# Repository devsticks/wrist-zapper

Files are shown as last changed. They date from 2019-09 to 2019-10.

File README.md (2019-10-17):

# Wrist Zapper
A portable wrist pose controlled electrocutaneous stimulator. Part of an undergraduate thesis.

Operates on an ESP32, and communicates with a companion app built on Blynk via BLE.

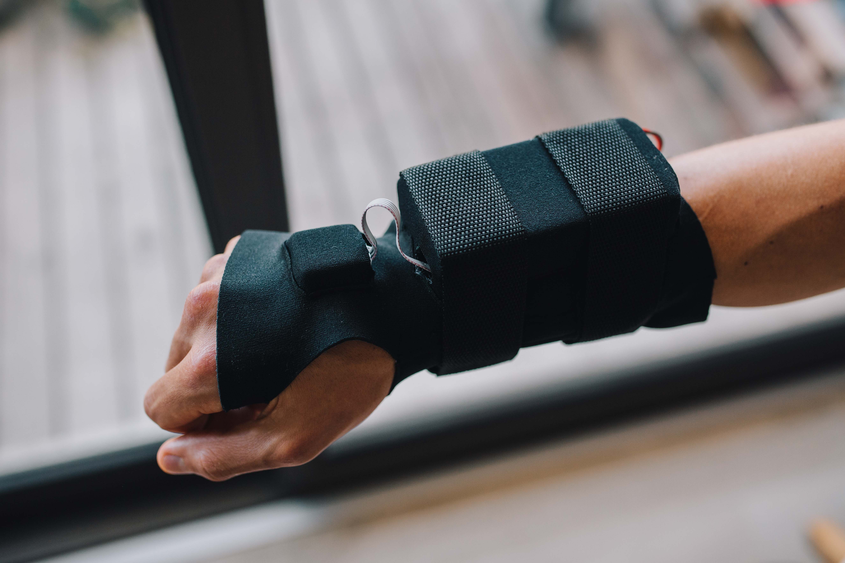
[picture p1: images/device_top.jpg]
The Wrist Zapper


If you'd like to make your own, see the build instructions [here](https://github.com/devsticks/wrist-zapper/tree/master/production_hardware/README.md).

## System Diagram

The following is a basic system diagram showing the various elements of the design and how they relate to one another:
<p align="center">
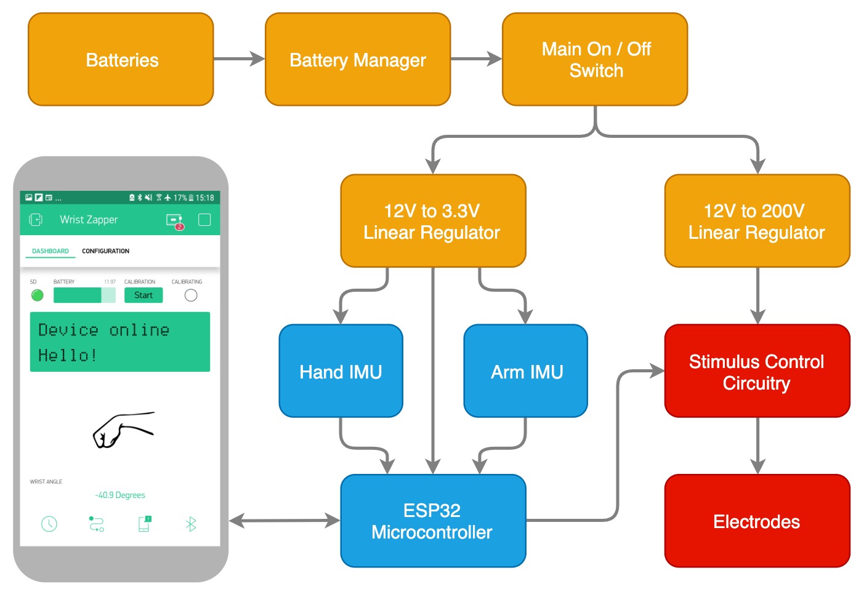
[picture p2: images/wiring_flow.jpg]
System diagram

</p>

## Bill of Materials

| Item                                                  | Part Number | Supplier  | Cost    | Quantity | Total Cost |
|-------------------------------------------------------|-------------|-----------|---------|----------|------------|
| Microcontroller (Adafruit ESP32 Feather)              | 3405        | Adafruit  | R299.25 | 1        | R299.25    |
| IMU (6 DOF)                                           | SEN-00138   | Netram    | R126.05 | 2        | R252.10    |
| Boost Convertor (12-200V, 60mA)                       | NCH6100HV   | Amazon    | R284.85 | 1        | R284.85    |
| Buck Convertor (12-3.3V, 2A)                          | MP1584      | Communica | R45.00  | 1        | R45.00     |
| NPN Transistor                                        | MJE340      | Farnell   | R10.66  | 1        | R10.66     |
| P-Channel MOSFET (400V, 3.5A)                         | FQP4P40     | Farnell   | R22.72  | 3        | R68.15     |
| SD Card Reader (Wemos D1 Mini RTC/Data Logger Shield) |             | Communica | R82.61  | 1        | R82.61     |
| Battery Manager (Comidox 3S, 12.6V, 10A)              |             | Amazon    | R38.95  | 1        | R38.95     |
| Resistor (Through-hole, 25mW, 1k)                     |             | UCT       | R0.00   | 4        | R0.00      |
| Resistor (Through-hole, 25mW, 2k2)                    |             | UCT       | R0.00   | 2        | R0.00      |
| Resistor (Through-hole, 25mW, 3k3)                    |             | UCT       | R0.00   | 1        | R0.00      |
| Resistor (Through-hole, 25mW, 10k)                    |             | UCT       | R0.00   | 1        | R0.00      |
| LED (Red, 5mm, 20mA)                                  |             | UCT       | R0.00   | 1        | R0.00      |
| LED (Green, 5mm, 20mA)                                |             | UCT       | R0.00   | 1        | R0.00      |
| Fuse (glass, 30mA)                                    |             | UCT       | R0.00   | 1        | R0.00      |
| Fuse holder                                           |             | UCT       | R0.00   | 1        | R0.00      |
| 3.7V Li-Ion Battery                                   |             | UCT       | R0.00   | 3        | R0.00      |
| Small On/Off Switch                                   | COM-00652   | Netram    | R15.00  | 1        | R15.00     |
| JST Connector (1A, 2 pin, female, 14cm)               |             | Communica | R3.04   | 4        | R12.17     |
| JST Connector (1A, 2 pin, male, 14cm)                 |             | Communica | R3.04   | 4        | R12.17     |
| Heat Shrink (Various colours, 1/8")                   |             | Communica | R0.44   | 3        | R1.32      |
| Header Connector (5 pin, female, 2.54mm, L, locking)  | XY136-05RT  | Communica | R0.91   | 2        | R1.82      |
| Header Connector (5 pin, male 2.54mm, locking)        | XY136-05HT  | Communica | R1.45   | 2        | R2.90      |
| Header Connector (2 pin, female, 2.54mm, L, locking)  | XY136-02RT  | Communica | R0.31   | 2        | R0.62      |
| Header Connector (2 pin, male 2.54mm, locking)        | XY136-02HT  | Communica | R0.55   | 2        | R1.10      |
| Ribbon Cable (10-way, 1m)                             |             | Communica | R7.36   | 0.1      | R0.74      |
| Any small jumper cable (comms core will do, 1m)       |             | UCT       | R0.00   | 1        | R0.00      |
| Strip Board (2.54mm pitch, 100x300mm)                 |             | UCT       | R70.00  | 1        | R70.00     |
| 3D Printing                                           |             |           | R120.00 | 1        | R120.00    |
|                                                       |             |           |         |          |            |
| **Total**                                             |             |           |         |          | **R1,319.40**  |

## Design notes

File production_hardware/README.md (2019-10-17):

# Build Instructions

You can make your very own Wrist Zapper - just be careful, you can really hurt yourself with one of these. 

If you want to get the cool stuff working first, follow this guide step-by-step. Otherwise go for it in any order - the steps aren't very dependent on one another. If you make your own Wrist Zapper please give me a shout - I'd love to see it!

# Table of Contents
1. [Device Electronics](#1-device-electronics)
2. [Microcontroller Code](#2-microcontroller-code)
3. [Smartphone App](#3-smartphone-app)
4. [Sleeve](#4-sleeve)
5. [Electrode](#5-electrode)
6. [Charger Electronics](#6-charger-electronics)
7. [Enclosures](#7-enclosures)
8. [Putting It Together](#8-putting-it-together)

## 1. Device Electronics

### Parts required

| Item                                                  | Part Number | Supplier  | Cost    | Quantity | Total Cost |
|-------------------------------------------------------|-------------|-----------|---------|----------|------------|
| Microcontroller (Adafruit ESP32 Feather)              | 3405        | Adafruit  | R299.25 | 1        | R299.25    |
| IMU (6 DOF)                                           | MPU6050     | Netram    | R126.05 | 2        | R252.10    |
| Boost Convertor (12-200V, 60mA)                       | NCH6100HV   | Amazon    | R284.85 | 1        | R284.85    |
| Buck Convertor (12-3.3V, 2A)                          | MP1584      | Communica | R45.00  | 1        | R45.00     |
| NPN Transistor (300V, 500mA, 20W)                     | MJE340      | Farnell   | R10.66  | 1        | R10.66     |
| P-Channel MOSFET (400V, 3.5A)                         | FQP4P40     | Farnell   | R22.72  | 3        | R68.15     |
| SD Card Reader (Wemos D1 Mini RTC/Data Logger Shield) |             | Communica | R82.61  | 1        | R82.61     |
| Battery Manager (Comidox 3S, 12.6V, 10A)              |             | Amazon    | R38.95  | 1        | R38.95     |
| Resistor (Through-hole, 25mW, 1k)                     |             | UCT       | R0.00   | 4        | R0.00      |
| Resistor (Through-hole, 25mW, 2k2)                    |             | UCT       | R0.00   | 2        | R0.00      |
| Resistor (Through-hole, 25mW, 3k3)                    |             | UCT       | R0.00   | 1        | R0.00      |
| Resistor (Through-hole, 25mW, 10k)                    |             | UCT       | R0.00   | 1        | R0.00      |
| LED (Red, 5mm, 20mA)                                  |             | UCT       | R0.00   | 1        | R0.00      |
| LED (Green, 5mm, 20mA)                                |             | UCT       | R0.00   | 1        | R0.00      |
| Fuse (glass, 30mA)                                    |             | UCT       | R0.00   | 1        | R0.00      |
| Fuse holder                                           |             | UCT       | R0.00   | 1        | R0.00      |
| 3.7V Li-Ion Battery                                   |             | UCT       | R0.00   | 3        | R0.00      |
| On/Off Switch                                         | COM-00652   | Netram    | R15.00  | 1        | R15.00     |
| JST Connector (1A, 2 pin, female, 14cm)               |             | Communica | R3.04   | 4        | R12.17     |
| JST Connector (1A, 2 pin, male, 14cm)                 |             | Communica | R3.04   | 4        | R12.17     |
| Heat Shrink (Various colours, 1/8")                   |             | Communica | R0.44   | 3        | R1.32      |
| Header Connector (5 pin, female, 2.54mm, L, locking)  | XY136-05RT  | Communica | R0.91   | 2        | R1.82      |
| Header Connector (5 pin, male 2.54mm, locking)        | XY136-05HT  | Communica | R1.45   | 2        | R2.90      |
| Header Connector (2 pin, female, 2.54mm, L, locking)  | XY136-02RT  | Communica | R0.31   | 2        | R0.62      |
| Header Connector (2 pin, male 2.54mm, locking)        | XY136-02HT  | Communica | R0.55   | 2        | R1.10      |
| Ribbon Cable (10-way, 1m)                             |             | Communica | R7.36   | 0.1      | R0.74      |
| Any small jumper cable (comms core will do, 1m)       |             | UCT       | R0.00   | 1        | R0.00      |
| Strip Board (2.54mm pitch, 100x300mm)                 |             | UCT       | R70.00  | 1        | R70.00     |
| | | | | | |
| **Total** |  |  |  |  | **R1,199.40** |

### Preparing the stripboard

Before soldering, you will need to remove portions of the stripboard in order to build the final circuit. The easiest way to mark out your stripboard is to download a copy of [this image](https://github.com/devsticks/wrist-zapper/raw/master/production_hardware/electronics/circuit_main_inverted_flipped.jpeg) and crop it so that the grid spacing on your screen matches that of your stripboard. The image at the link perfectly matches 2.54mm stripboard on a 9.7"-sized iPad screen. 

Once you have the image sized up, place your stripboard over the screen (metal side up) and mark any spots with purple crosses for removal with a marker pen, as below (this is easier to see in real life than in the image...). The task is best done in a dark room with screen brightness maximised.

<p align="center">
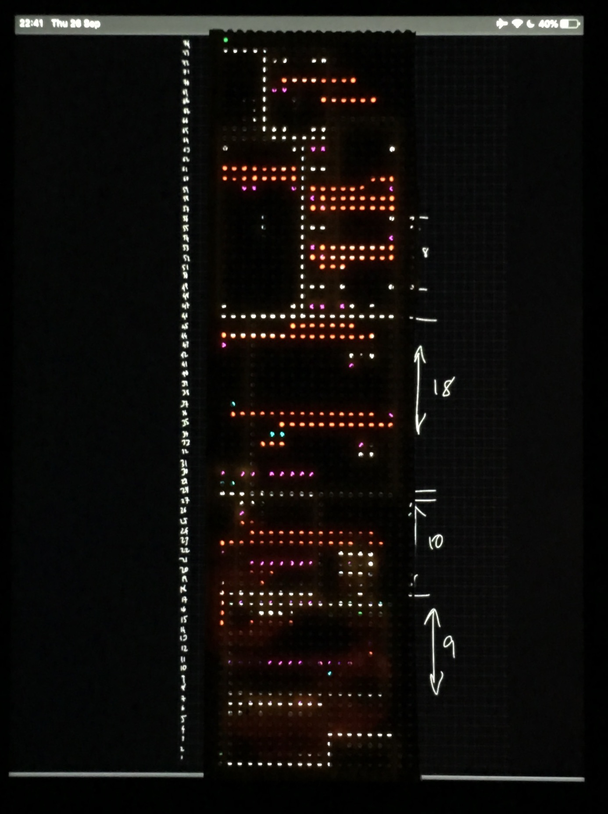
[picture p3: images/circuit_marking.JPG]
Circuit Marking
  
</p>

Once marked, use a small drill bit to remove the contact strip at the relevant holes. I would highly recommend checking that you've broken continuity at the marked spots - you could easily destroy some expensive components by getting this wrong, and the further you go the harder it becomes to find these errors.

<p align="center">
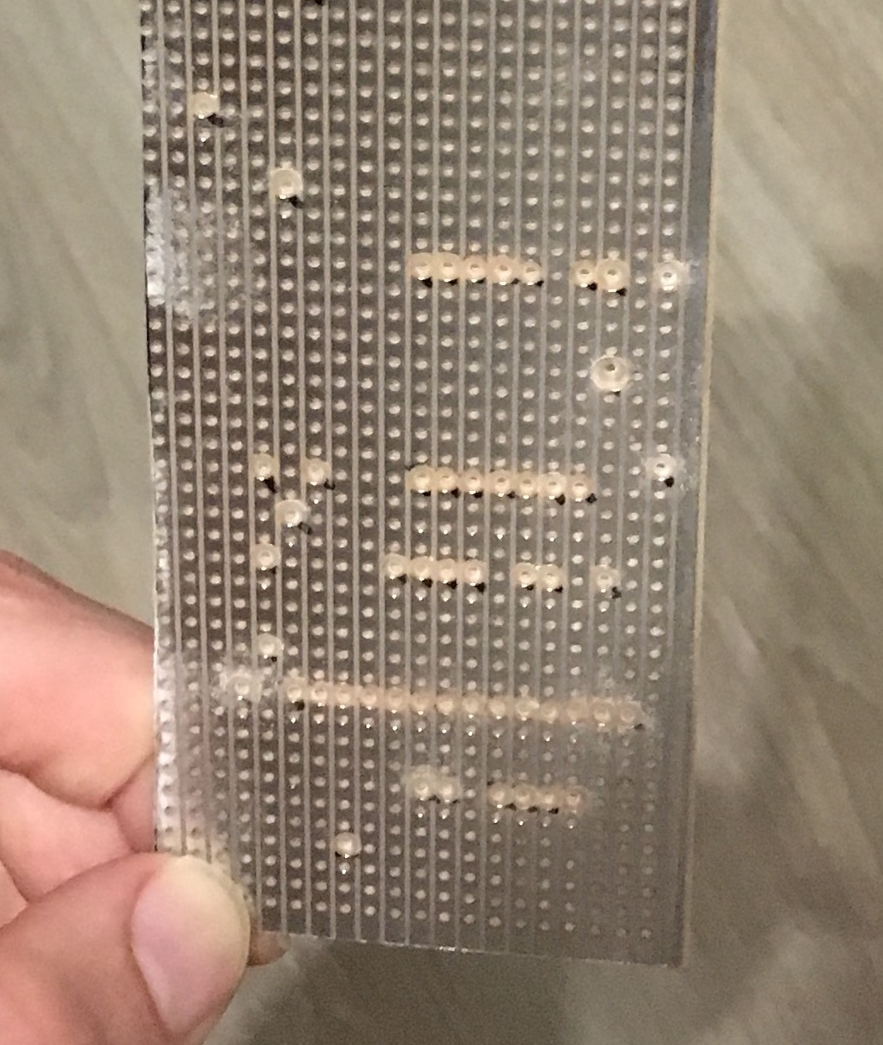
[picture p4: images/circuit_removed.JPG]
Circuit Removed
  
</p>

The next step is to do a similar thing with [this image](https://github.com/devsticks/wrist-zapper/raw/master/production_hardware/electronics/circuit_main_inverted.jpeg) to mark out the positions of joining wires. This time place the stripboard metal side down on your screen and draw lines over the red areas. 

### Soldering it up

Once you've marked the wires out, neatly solder the thin comms wires into place where required. As far as possible, keep the wires flat - there's not much vertical room for manoeuvre here. The mess of wires connecting the microSD breakout should be connected as follows:

| ESP32 | microSD Shield |
|-------|----------------|
|4|D8|
|5|D5|
|18|D7|
|19|D6|

If you'd like to make your circuit board black (it just looks so much more professional!), now is the time to do so - I used a thick marker pen.

Prepare the buck and boost convertors by tuning them to give 3.3V and 200V respectively when supplied with a 12V input.

From this point it's just a matter of soldering things into place following the layout below. The board loayout is extremely cramped, and some components or breakout boards may need to be (carefully) filed or sanded down to fit. I would recommend starting with the shortest components first, then moving on to the tallest. Note that I've used female headers for the ESP32 and microSD card boards, while the MPU6050 (IMU) and NCH6100HV (Boost Convertor) were soldered straight on with male headers to save space (I know, I know...).

Before you solder in the NCH6100HV - probably the last part you'll add - test that things are on track by connecting a 12V supply to the input jack and switching on the board. If the current spikes as you do so switch it off immediately. If not, good job! Next, test that you're getting 3.3V - and no more! - at all the places you're expecting it, and 0 at all the ground pins. If that's all looking good, continue!

<p align="center">
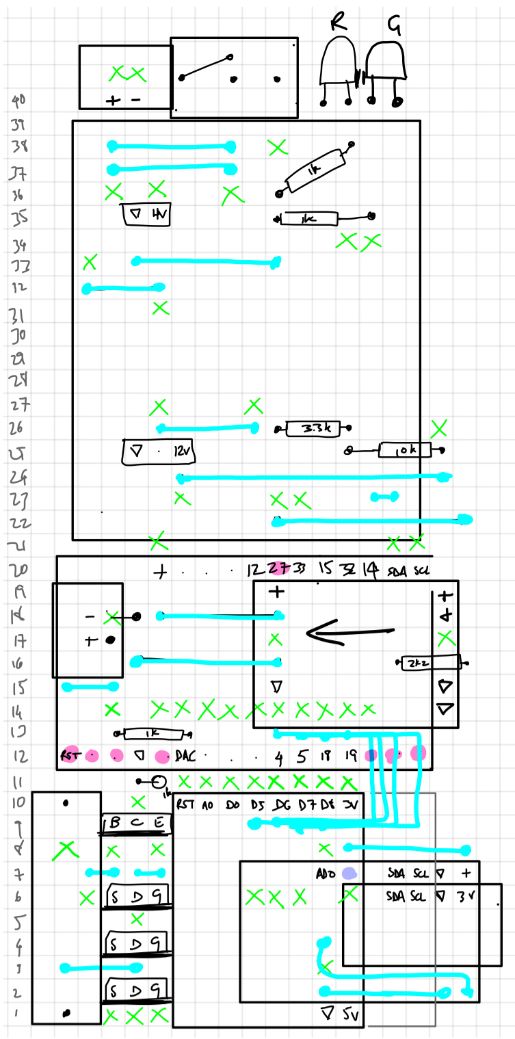
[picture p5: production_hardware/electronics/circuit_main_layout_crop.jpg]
Circuit Layout
  
</p>

The finished product should look something like this:
<p align="center">
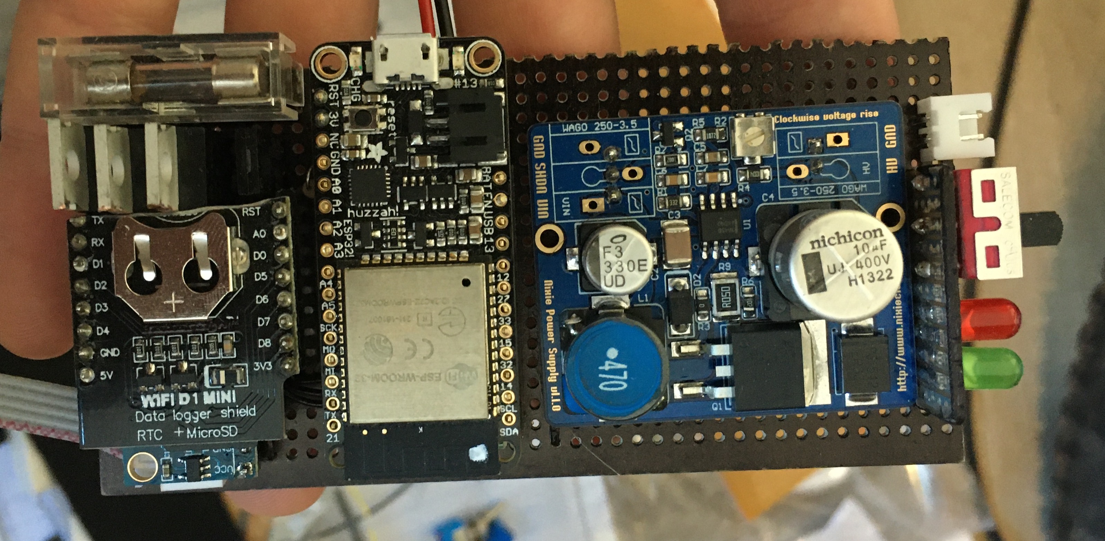
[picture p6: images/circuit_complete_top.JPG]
Circuit Top
  
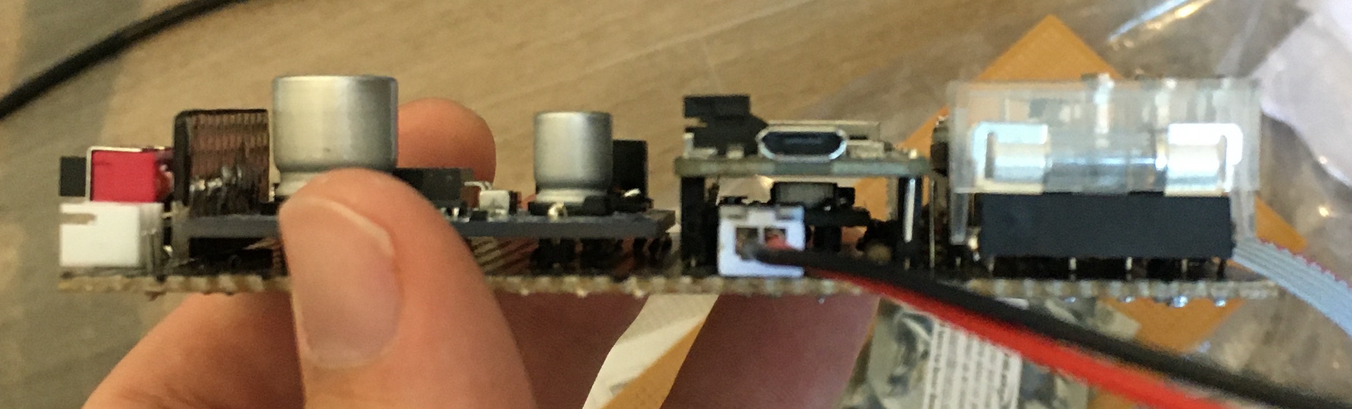
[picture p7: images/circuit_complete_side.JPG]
Circuit Side
  
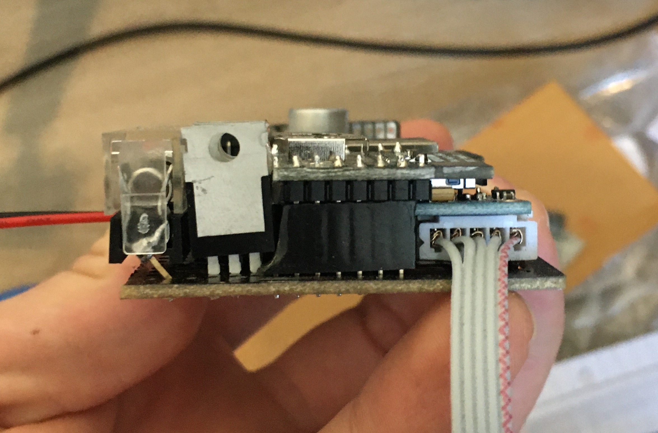
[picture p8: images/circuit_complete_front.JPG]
Circuit Front
  
</p>

If you've made it this far give someone a high five - you're doing really well! 

## 2. Microcontroller Code

## 3. Smartphone App

## 4. Sleeve

## 5. Electrode

## 6. Charger Electronics

## 7. Enclosures

## 8. Putting It Together

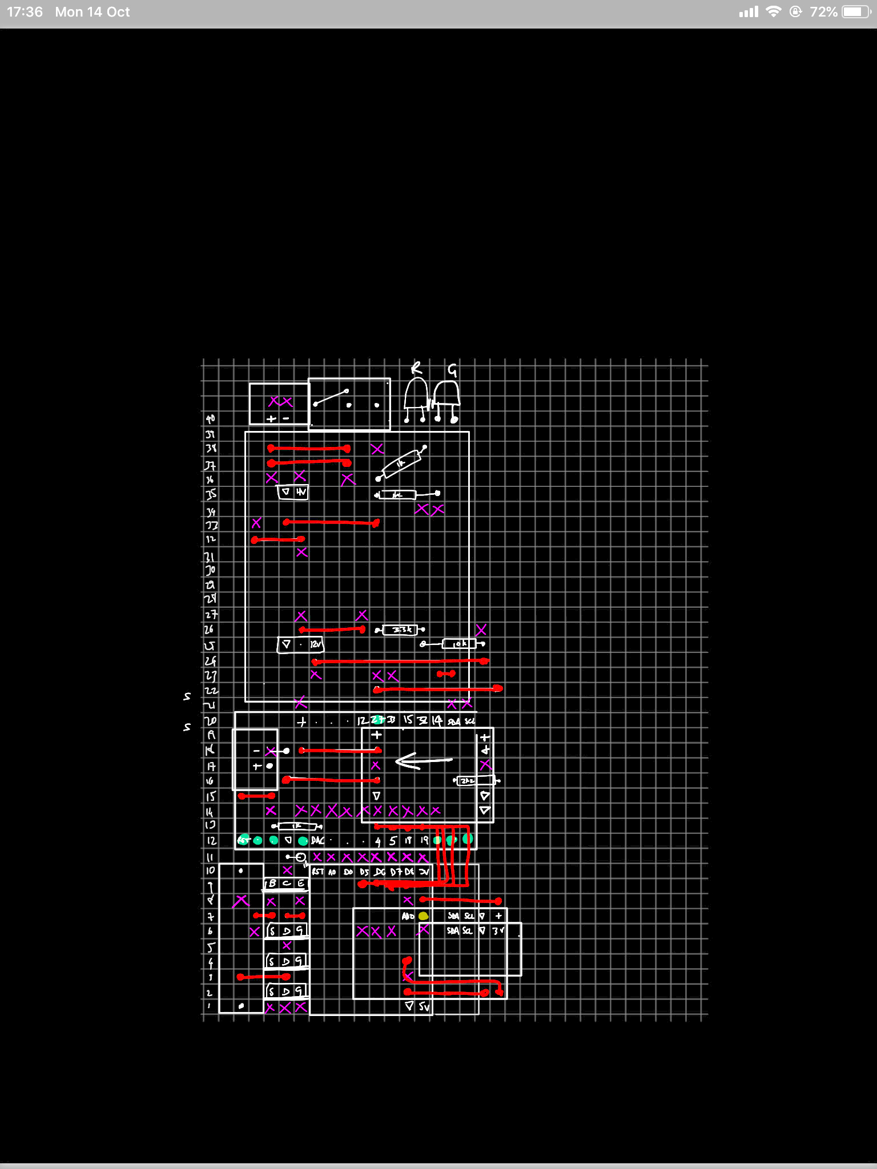
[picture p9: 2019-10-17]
production_hardware/electronics/circuit_main_inverted.jpeg

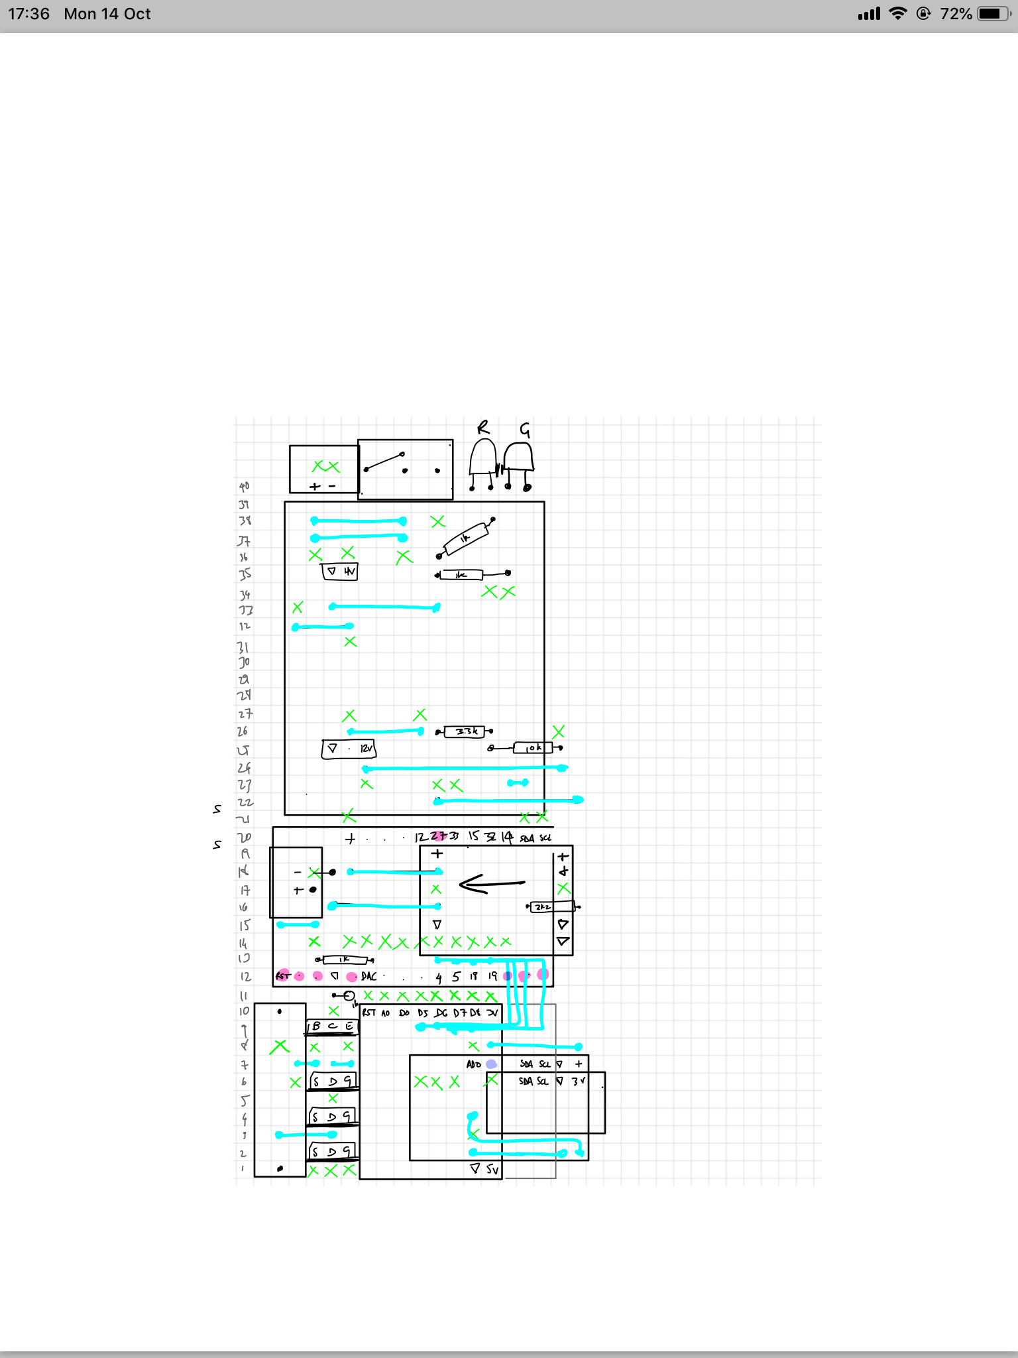
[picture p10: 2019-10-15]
production_hardware/electronics/circuit_main_layout.jpeg

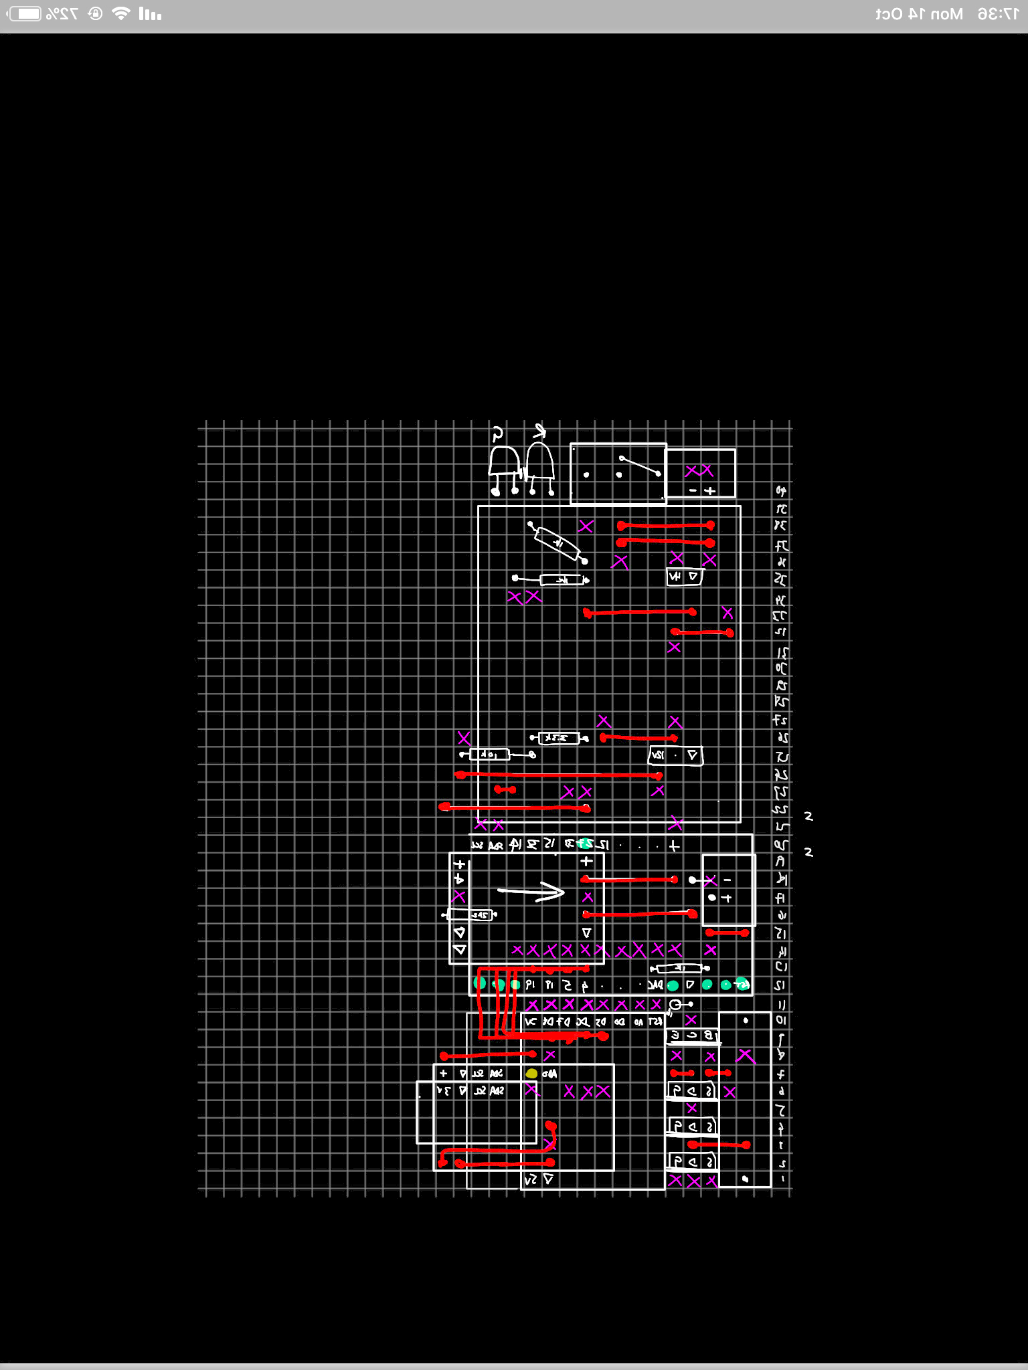
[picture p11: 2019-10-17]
production_hardware/electronics/circuit_main_inverted_flipped.jpeg

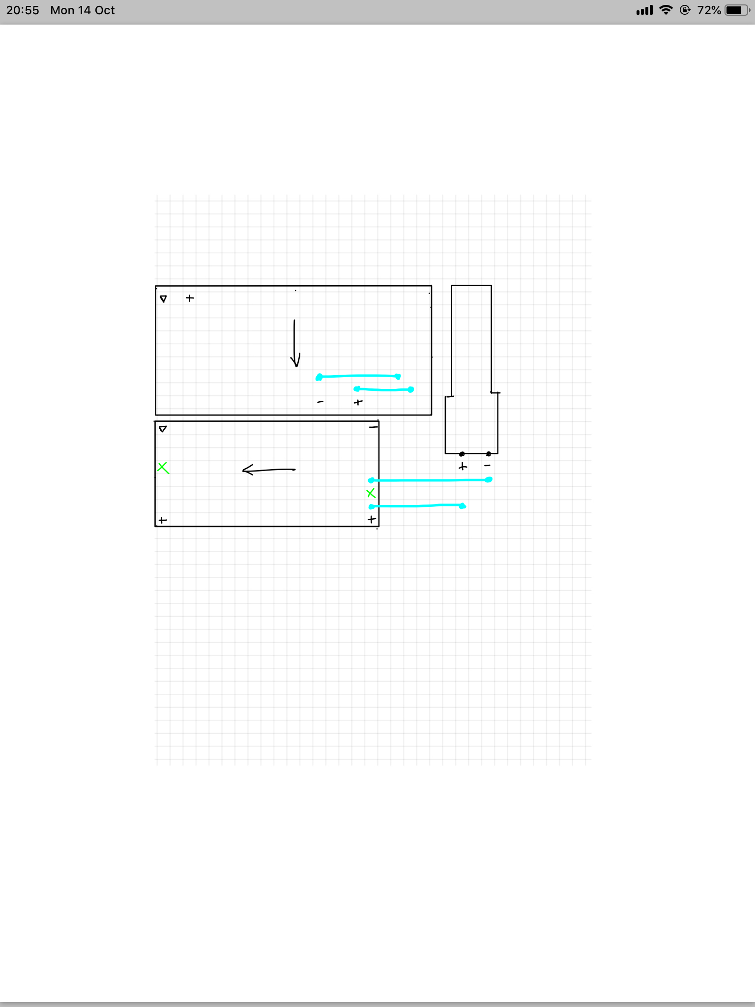
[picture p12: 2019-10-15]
production_hardware/electronics/circuit_charger_layout.jpeg

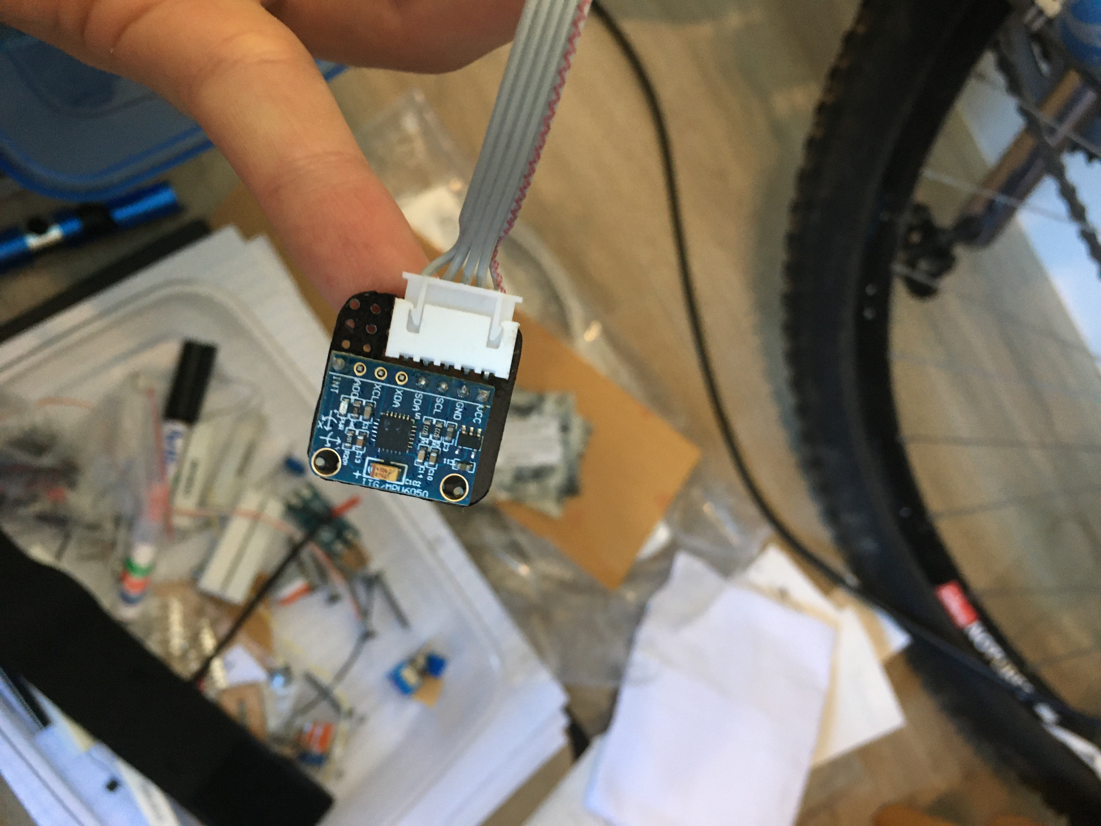
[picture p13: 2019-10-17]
images/circuit_complete_hand.JPG

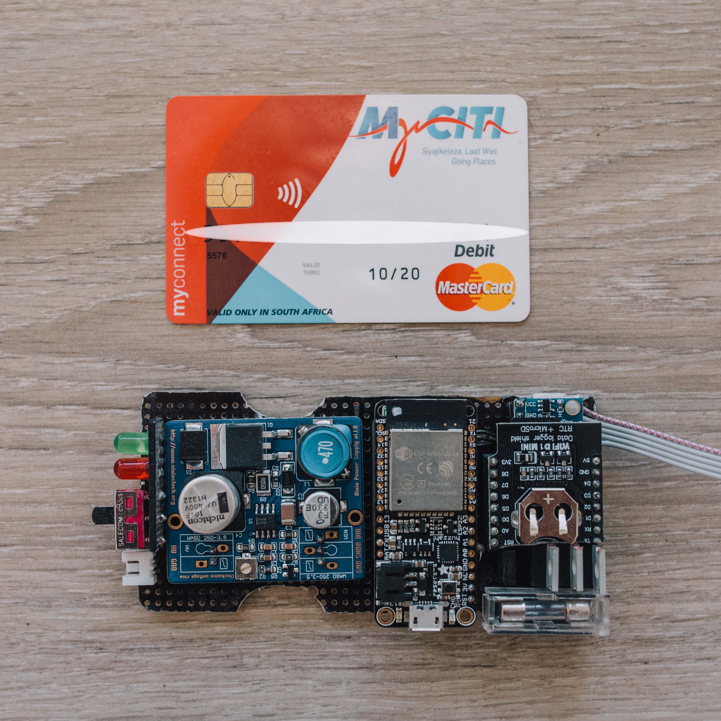
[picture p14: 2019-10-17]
images/circuit_final_top.jpg

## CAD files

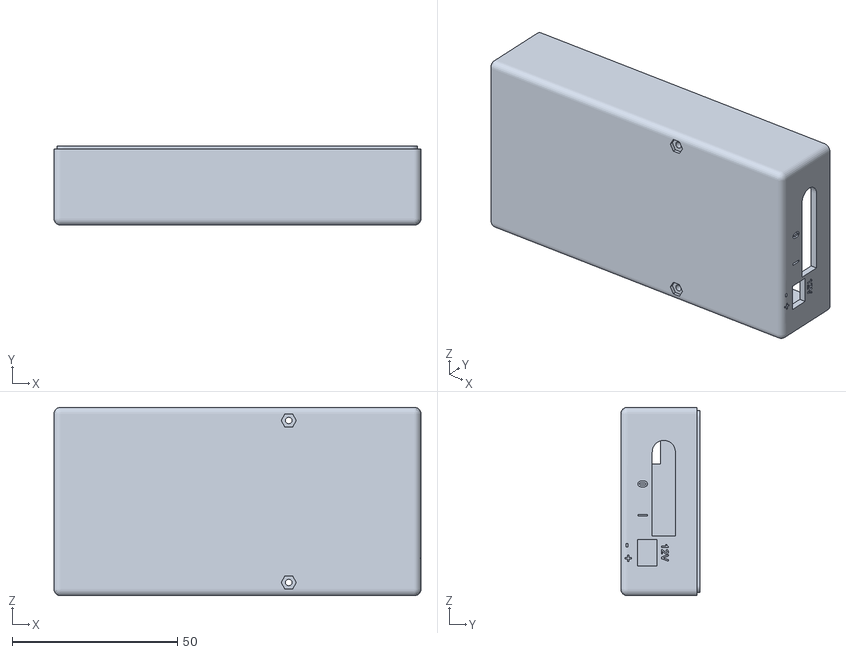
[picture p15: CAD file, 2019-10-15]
production_hardware/arm_box/Arm Base 3.stl
111.0 x 24.0 x 57.0

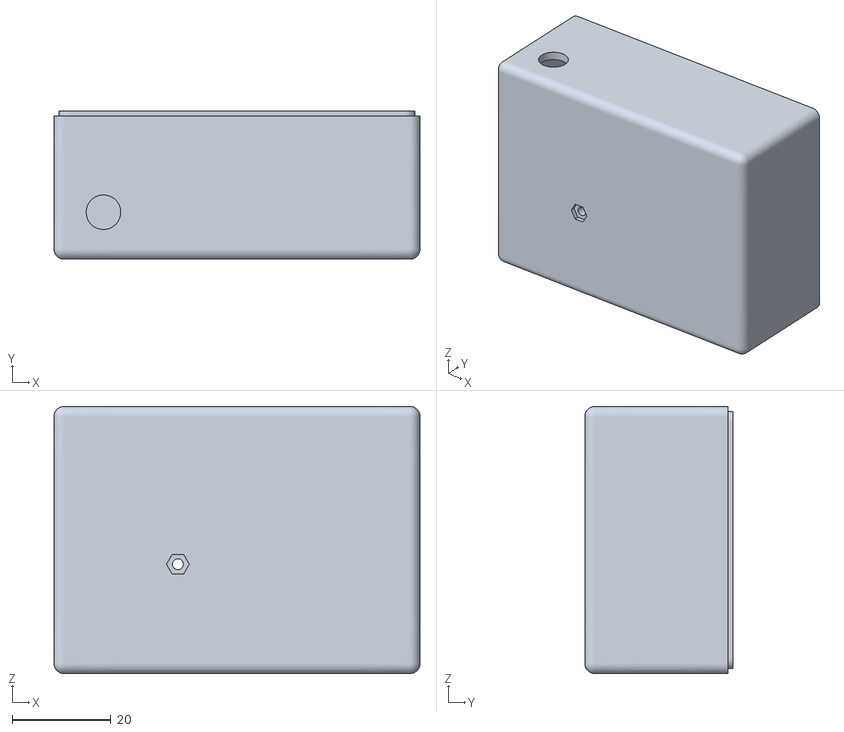
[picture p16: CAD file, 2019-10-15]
production_hardware/charger_box/Charger Base 3.stl
74.0 x 30.0 x 54.0

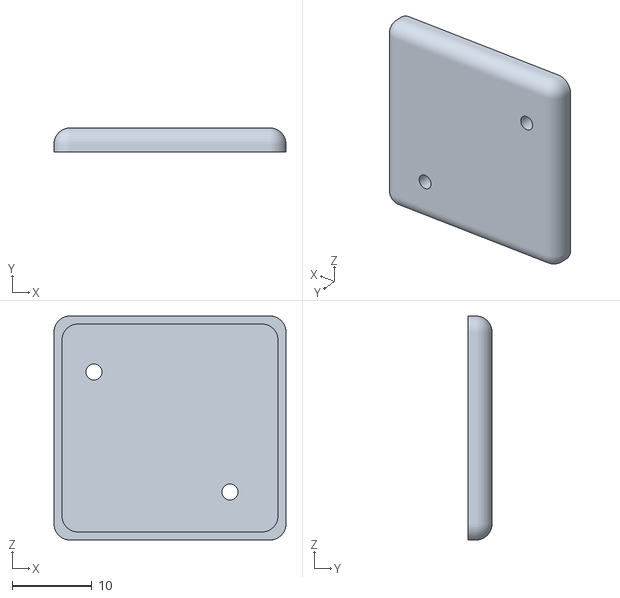
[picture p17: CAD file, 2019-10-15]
production_hardware/hand_box/Hand Lid 3.stl
29.0 x 3.00 x 28.0

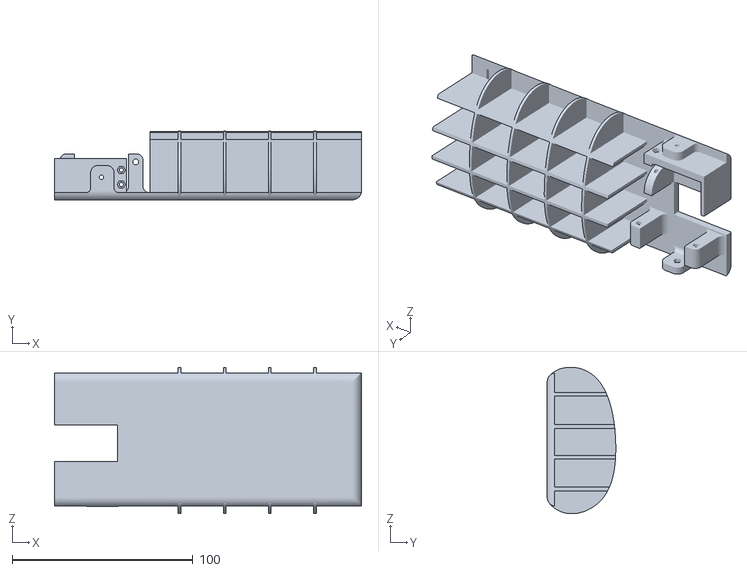
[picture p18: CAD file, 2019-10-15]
production_hardware/test_apparatus/Arm 2.stl
170.0 x 38.0 x 81.1

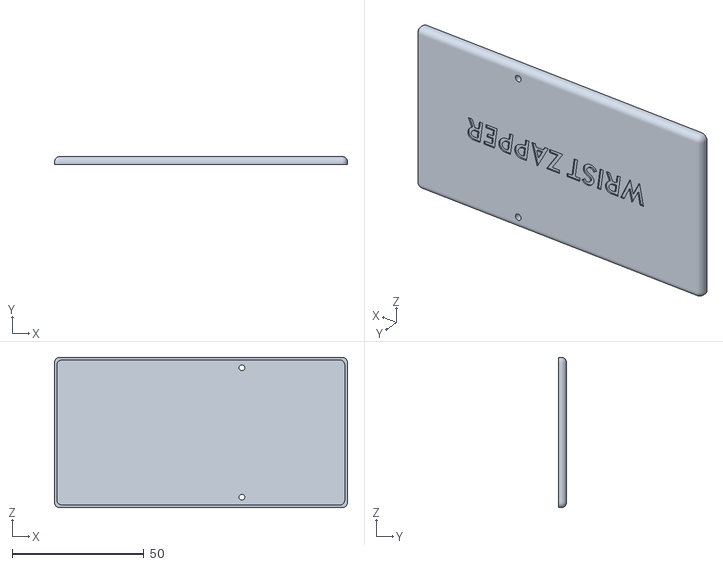
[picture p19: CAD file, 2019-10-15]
production_hardware/arm_box/Arm Lid 3.stl
111.0 x 3.00 x 57.0

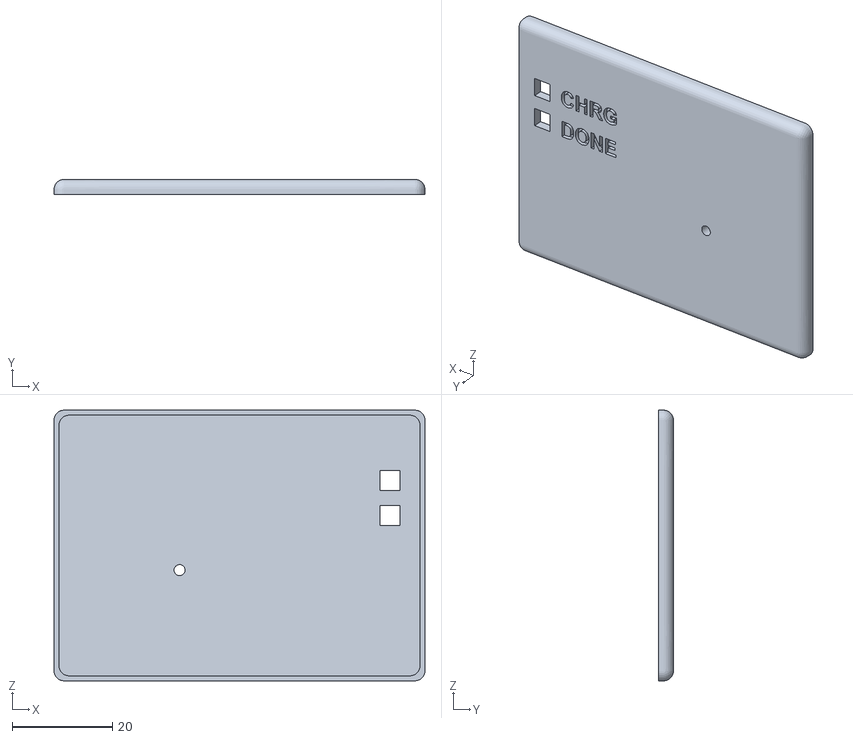
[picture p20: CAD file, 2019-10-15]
production_hardware/charger_box/Charger Lid 3.stl
74.0 x 3.00 x 54.0

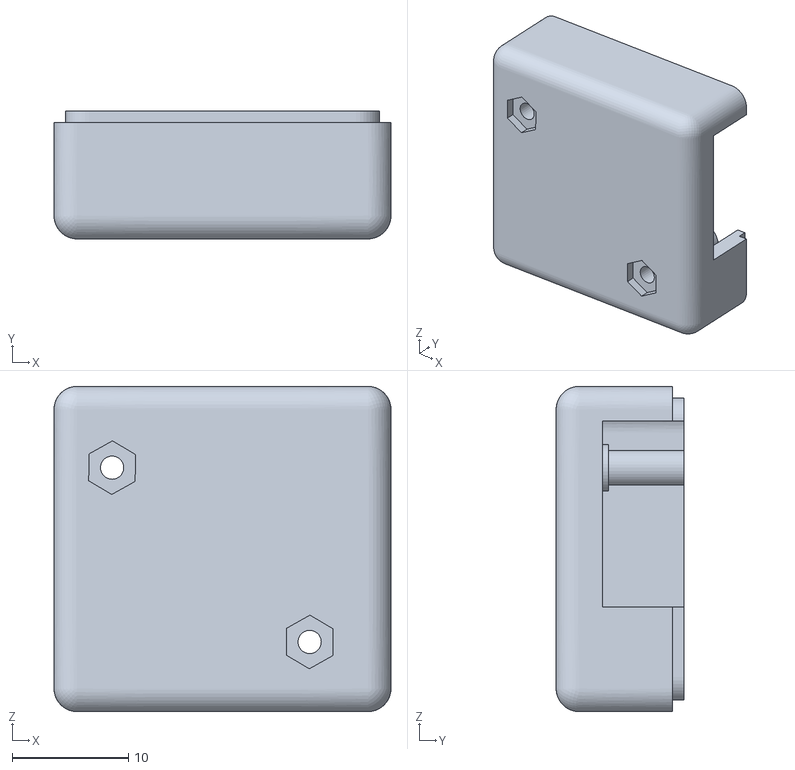
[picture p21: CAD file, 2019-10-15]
production_hardware/hand_box/Hand Base 3.stl
29.0 x 11.0 x 28.0

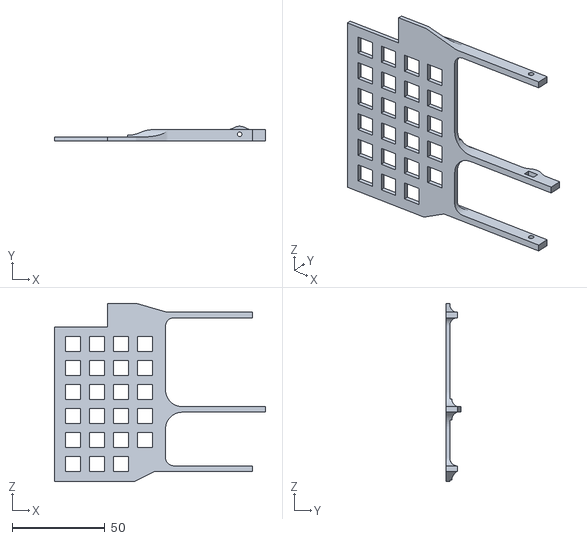
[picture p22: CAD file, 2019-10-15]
production_hardware/test_apparatus/Hand 2.stl
114.0 x 7.83 x 96.4

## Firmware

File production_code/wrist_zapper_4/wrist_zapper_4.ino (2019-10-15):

/************************************************************
 * 
 *  https://github.com/devsticks/wrist-zapper
 *  
 *  @ description: code for a device which uses two IMUs to calculate the extension angle of 
 *                 a wearer's wrist, and shock them when they enter a set range of movement
 *  @ author: Devin Stickells
 *  @ license: GNU General Public License v3.0
 *  @ supported devices: Espressif ESP32 (Tested on Adafruit Feather Huzzah32)
 */

//// -- INCLUDES -- ////

#include "BlynkSimpleEsp32_BLE.h"                   // https://github.com/blynkkk/blynk-library
#include "BLEDevice.h"
#include "BLEServer.h"

#include "I2Cdev.h"                                 // helper functions for IMU interfacing https://github.com/jrowberg/i2cdevlib
#include "MPU6050_6Axis_MotionApps_V6_12.h"         // functions specific to the MPU6050, from I2CDevLib https://github.com/jrowberg/i2cdevlib/tree/master/Arduino/MPU6050
#include "SD.h"                                     // SD card interfacing
#include "TimeLib.h"                                // Paul Stoffregen's Arduino time library https://github.com/PaulStoffregen/Time
#include "WidgetRTC.h"                              // to get real time from Blynk
#include "helper_3dmath.h"                          // quaternion math, part of I2CDevLib https://github.com/jrowberg/i2cdevlib/tree/master/Arduino/MPU6050
#include "BasicLinearAlgebra.h"                     // matrix math, https://github.com/tomstewart89/BasicLinearAlgebra
#include "driver/ledc.h"                            // PWM control
#include "Wire.h"                                   // nice GPIO functions

//// -- CONSTANT DEFINITIONS -- ////

using namespace BLA;                                // BasicLinearAlgebra namespace
#define BATTERY_CUTOFF_VOLTAGE 10.5                 // Voltage at which the device starts to complain about a low battery

// hardware pins
#define INTERNAL_LED_PIN 13 
#define EXTERNAL_RED_LED_PIN 15
#define EXTERNAL_GREEN_LED_PIN 14
#define BATTERY_TEST_PIN 32                         // analog input from battery voltage divider
#define STIM_PIN 25                                 // analog output to base of stim control BJT
#define SDA_PIN 22                                  // I2C SDA pin
#define SCL_PIN 23                                  // I2C SCL pin

// Blynk virtual pins
#define BLYNK_EXT_ANGLE_PIN V1
#define BLYNK_BATTERY_PIN V2
#define BLYNK_LCD_PIN V3
#define BLYNK_SD_LED_PIN V4
#define BLYNK_EXT_ANGLE_IMG_PIN V5
#define BLYNK_START_CALIB_PIN V6
#define BLYNK_CALIB_LED_PIN V7
#define BLYNK_SHOCK_START_ANGLE_PIN V8
#define BLYNK_SHOCK_MAX_ANGLE_PIN V9
#define BLYNK_SHOCK_START_INTENSITY_PIN V10
#define BLYNK_SHOCK_MAX_INTENSITY_PIN V11
#define TEST_PIN V12
#define BLYNK_SHOCK_START_IMG_PIN V13
#define BLYNK_SHOCK_MAX_IMG_PIN V14

#define BLYNK_USE_DIRECT_CONNECT
/* Comment this out to disable Blynk prints and save space */
#define BLYNK_PRINT Serial

float testvar = 0;

//// -- GLOBAL VARIABLES -- ////

// IMU AD0 pin low = 0x68 (hand IMU)
// IMU AD0 pin high = 0x69 (arm IMU)
MPU6050 imu1(0x69), imu2(0x68);                     // initialise IMU objects with their I2C addresses

// LED state vars for toggle / blinking functionality
bool internalLEDState = false;
bool externalRedLEDState = false;
bool externalGreenLEDState = false;

// IMU control / status vars
bool dmp1Ready = false, dmp2Ready = false;          // flag set true if DMP init was successful
uint8_t mpu1IntStatus, mpu2IntStatus;               // holds actual interrupt status byte from IMU
uint8_t devStatus;                                  // return status after each device operation (0 = success, !0 = error)
uint16_t packet1Size, packet2Size;                  // expected DMP packet size (default is 42 bytes)
uint16_t fifoCount1, fifoCount2;                    // count of all bytes currently in FIFO
uint8_t fifoBuffer1[64], fifoBuffer2[64];           // FIFO storage buffer
volatile bool mpu1Interrupt = false;                // indicates whether MPU1 interrupt pin has gone high
volatile bool mpu2Interrupt = false;                // indicates whether MPU2 interrupt pin has gone high
float shockPercentage = 0;
char shockStartAngle = 30, shockMaxAngle = 60;      // wrist angle range in which to shock wearer (in degrees upward from horizontal)
char shockStartIntensity = 0, shockMaxIntensity = 10; // variation in shock intensity over critical range - corresponding to start and max angles
bool calibrating = false;
bool calibrated = false;
bool sdStatus = true;
String logFileName = "/angle_log.txt";

// orientation / motion vars
Quaternion q_arm, q_hand, q_calib;                  // [w, x, y, z] quaternion containers for arm, hand IMUs, and calibration between them
float extensionAngle = 0;                           // wrist extension angle

// Blynk vars
BlynkTimer fastTimer, slowTimer;
WidgetLCD lcd(BLYNK_LCD_PIN);                       // init Blynk LCD variable
WidgetLED sdLED(BLYNK_SD_LED_PIN);                  // init Blynk SD indicator LED
WidgetLED calibLED(BLYNK_CALIB_LED_PIN);            // init Blynk calibration indicator LED
WidgetRTC rtc;                                      // init Blynk real time clock object
// Auth Token for the microcontroller device.
// Go to Project Settings (nut icon) in the Blynk App to generate one.
char auth[] = "fMTNpL-rwcWIsqoN3n3SwtQAUDk7_YZg";   // Tom's ESP32
bool slowTicToc = false;


//// -- FUNCTION PROTOTYPES -- ////
/* the Arduino IDE doesn't build function prototypes if they take references as arguments, so we have to make them ourselves... */

void appendFile(fs::FS &fs, String path, /*const char * */ String message);


//// -- TIMER FUNCTIONS -- ////

// In the app, Widget's reading frequency should be set to PUSH. This means
// that you define how often to send data to Blynk App.
void fastTimerEvent() // 500ms - Battles with more that 10 values per second.
{
    Blynk.virtualWrite(BLYNK_EXT_ANGLE_PIN, extensionAngle);

    setWristImage(BLYNK_EXT_ANGLE_IMG_PIN, extensionAngle);

    // Blink the red light if battery is dead
    if (getBatteryVoltage() < BATTERY_CUTOFF_VOLTAGE)
    {
      toggleLED(externalRedLEDState, EXTERNAL_RED_LED_PIN);
    } 
    else if (externalRedLEDState && !calibrating) // if red LED is on and battery is fine, kill it
    {
      externalRedLEDState = false;
      digitalWrite(EXTERNAL_RED_LED_PIN, 0);
    }
}

void slowTimerEvent() // 10s
{
  slowTicToc != slowTicToc;
  if (!calibrating) // don't overwrite instructions on LCD screen 
  {
    if (getBatteryVoltage() > BATTERY_CUTOFF_VOLTAGE) // above 10.5V, i.e. 3.5V per cell
    {
      if (devStatus != 0 || !dmp1Ready || ! dmp2Ready) 
      { /* startupFailed() */  
        lcdPrint(0, "Device error");
        lcdPrint(1, "Try a reboot"); 
      } else {
        lcdPrint(0, "Device online");
        lcdPrint(1, "Hello!");
      }
    } else {  // battery is dead (less than 3.5V per cell, panic)
      lcdPrint(0, "Battery depleted");
      lcdPrint(1, "Replace now");
    }
  }

  if (sdStatus) // mircoSD card is working fine
  {
    Blynk.setProperty(BLYNK_SD_LED_PIN, "color", "#43D35C");        // make Blynk app's SD indicator LED green
  }
  else
  {
    Blynk.setProperty(BLYNK_SD_LED_PIN, "color", "#D3435C");        // make Blynk app's SD indicator LED red
  }
}

//// -- SETUP -- ////
// runs when the device starts up
void setup() 
{
    Serial.begin(115200);                             // initialize serial comms   
  
    Serial.println("Waiting for connections...");
    Blynk.setDeviceName("Wrist Zapper");
    Blynk.begin(auth);

    // Setup a function to be called every second
    fastTimer.setInterval(500L, fastTimerEvent);
    slowTimer.setInterval(10000L, slowTimerEvent);
    
    // This will print Blynk Software version to the Terminal Widget when
    // your hardware gets connected to Blynk Server
    Serial.println(F("Blynk v" BLYNK_VERSION ": Device started"));
    Serial.println(F("-------------"));
    Serial.println(F("Type 'Marco' and get a reply, or type"));
    Serial.println(F("anything else and get it printed back."));
    Serial.flush();

    setSyncInterval(10 * 60); // update real time clock every 10 minutes

    setupGPIO();
    initializeIMUs();
    testIMUConnections();

    setupIMU(imu1, mpu1IntStatus, dmp1Ready, packet1Size, "IMU 1");
    setupIMU(imu2, mpu2IntStatus, dmp2Ready, packet2Size, "IMU 2");
    
    setupSD();

    if (devStatus != 0 || !dmp1Ready || ! dmp2Ready) 
    { /* startupFailed() */  
      lcdPrint(0, "Device error");
      lcdPrint(1, "Try a reboot"); 
      toggleLED(externalRedLEDState, EXTERNAL_RED_LED_PIN);   
    } 
    else // happy days
    {
      lcdPrint(0, "Device online");
      lcdPrint(1, "Hello!");
    }

//    // set wrist angle images in configuration tab of app
//    Blynk.virtualWrite(BLYNK_SHOCK_START_ANGLE_PIN, shockStartAngle);
//    setWristImage(BLYNK_SHOCK_START_IMG_PIN, shockStartAngle);
//    Blynk.virtualWrite(BLYNK_SHOCK_MAX_ANGLE_PIN, shockMaxAngle);
//    setWristImage(BLYNK_SHOCK_MAX_IMG_PIN, shockMaxAngle);
    
    // flash LEDs, we're awake!
    for (int i = 0; i < 5; i += 1) 
    {
      toggleLED(externalRedLEDState, EXTERNAL_RED_LED_PIN);
      toggleLED(externalGreenLEDState, EXTERNAL_GREEN_LED_PIN);
      delay(200);
    }

    delay(2000); // let things settle 
}

// The main hardware loop

void loop() {
    Blynk.run();
    fastTimer.run(); // Initiates BlynkTimer
    slowTimer.run(); 

    if (devStatus != 0 || !dmp1Ready || ! dmp2Ready) 
    { /* startupFailed() */  
      return;
    }

    // reset interrupt flag and get INT_STATUS byte
    mpu1Interrupt = false;
    mpu1IntStatus = imu1.getIntStatus();

    mpu2Interrupt = false;
    mpu2IntStatus = imu2.getIntStatus();

    // get current FIFO count
    fifoCount1 = imu1.getFIFOCount();
    fifoCount2 = imu2.getFIFOCount();

    bool overflow = false;

    // check for overflow (this should never happen unless our code is too inefficient)
    if ((mpu1IntStatus & _BV(MPU6050_INTERRUPT_FIFO_OFLOW_BIT)) || fifoCount1 >= 1024) 
    {
        // reset so we can continue cleanly
        imu1.resetFIFO();
        Serial.println(F("FIFO 1 overflow!"));
         overflow = true;
    }
    
    if ((mpu2IntStatus & _BV(MPU6050_INTERRUPT_FIFO_OFLOW_BIT)) || fifoCount2 >= 1024) 
    {
        // reset so we can continue cleanly
        imu2.resetFIFO();
        Serial.println(F("FIFO 2 overflow!"));
        overflow = true;
    }
    
    if (overflow) 
    {
      overflow = false;
      return;
    }
//      otherwise, check for DMP data ready interrupt (this should happen frequently)
    else if (mpu1IntStatus & _BV(MPU6050_INTERRUPT_DMP_INT_BIT) || mpu2IntStatus & _BV(MPU6050_INTERRUPT_DMP_INT_BIT) ) 
    {
        while (fifoCount1 > 100 || fifoCount2 > 100) updateIMUs();                                             // get fresh quaternion orientations

        extensionAngle = calcExtensionAngle(q_arm, q_hand); 

        // build date time string for easy conversion to CSV
        String dateString = "";
        switch (timeStatus()) { 
          case timeSet:
          {
               dateString = "Set, ";
               break;
          }
          case timeNeedsSync: 
          { 
             dateString = "Needs Sync, ";
             break;
          }
          default: 
          { 
             dateString = "Not Set, ";
             break;
          }
        }

        dateString += getDateTimeString();
        //"/angle_log.txt"
        appendFile(SD, logFileName, dateString + ", " + String(extensionAngle) + "\n");
        
        Serial.println(String(extensionAngle));
        updateShock(extensionAngle);
        
//        Serial.println(String(getBatteryPercentage()));

        // blink internal LED to indicate activity
        toggleLED(internalLEDState, INTERNAL_LED_PIN);
    }
}

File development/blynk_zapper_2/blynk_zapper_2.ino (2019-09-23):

/* MPU9250 Basic Example Code
 by: Kris Winer
 date: April 1, 2014
 license: Beerware - Use this code however you'd like. If you 
 find it useful you can buy me a beer some time.
 
 Demonstrate basic MPU-9250 functionality including parameterizing the register addresses, initializing the sensor, 
 getting properly scaled accelerometer, gyroscope, and magnetometer data out. Added display functions to 
 allow display to on breadboard monitor. Addition of 9 DoF sensor fusion using open source Madgwick and 
 Mahony filter algorithms. Sketch runs on the 3.3 V 8 MHz Pro Mini and the Teensy 3.1.
 
 SDA and SCL should have external pull-up resistors (to 3.3V).
 10k resistors are on the EMSENSR-9250 breakout board.
 
 Hardware setup:
 MPU9250 Breakout --------- Arduino
 VDD ---------------------- 3.3V
 VDDI --------------------- 3.3V
 SDA ----------------------- A4
 SCL ----------------------- A5
 GND ---------------------- GND
 
 Note: The MPU9250 is an I2C sensor and uses the Arduino Wire library. 
 Because the sensor is not 5V tolerant, we are using a 3.3 V 8 MHz Pro Mini or a 3.3 V Teensy 3.1.
 We have disabled the internal pull-ups used by the Wire library in the Wire.h/twi.c utility file.
 We are also using the 400 kHz fast I2C mode by setting the TWI_FREQ  to 400000L /twi.h utility file.
 */
#include "Wire.h"   
#include "MPU9250.h"
/*#include <SPI.h>*/
#include "FS.h"
#include "SD.h"
#include "SPI.h"

// See also MPU-9250 Register Map and Descriptions, Revision 4.0, RM-MPU-9250A-00, Rev. 1.4, 9/9/2013 for registers not listed in 
// above document; the MPU9250 and MPU9150 are virtually identical but the latter has a different register map
//
//Magnetometer Registers
#define AK8963_ADDRESS   0x0C
#define AK8963_WHO_AM_I  0x00 // should return 0x48
#define AK8963_INFO      0x01
#define AK8963_ST1       0x02  // data ready status bit 0
#define AK8963_XOUT_L   0x03  // data
#define AK8963_XOUT_H  0x04
#define AK8963_YOUT_L  0x05
#define AK8963_YOUT_H  0x06
#define AK8963_ZOUT_L  0x07
#define AK8963_ZOUT_H  0x08
#define AK8963_ST2       0x09  // Data overflow bit 3 and data read error status bit 2
#define AK8963_CNTL      0x0A  // Power down (0000), single-measurement (0001), self-test (1000) and Fuse ROM (1111) modes on bits 3:0
#define AK8963_ASTC      0x0C  // Self test control
#define AK8963_I2CDIS    0x0F  // I2C disable
#define AK8963_ASAX      0x10  // Fuse ROM x-axis sensitivity adjustment value
#define AK8963_ASAY      0x11  // Fuse ROM y-axis sensitivity adjustment value
#define AK8963_ASAZ      0x12  // Fuse ROM z-axis sensitivity adjustment value

#define SELF_TEST_X_GYRO 0x00                  
#define SELF_TEST_Y_GYRO 0x01                                                                          
#define SELF_TEST_Z_GYRO 0x02
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

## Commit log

2019-07-24 Working link from single MPU9250 to ESP32 to Blynk
2019-09-09 Logging to SD card and current control
2019-09-11 Kind of working unconstrained angle estimation in matlab
    [log.csv]
2019-09-23 Angle estimation working in MATLAB
    [qlog.csv, qlog2.csv]
2019-09-26 Angle estimation working online. Issue with slow response from second IMU.
    [alog3.csv, qlog3.csv]
2019-10-01 Added battery voltage read, fixed up LED pins, no more interrupts
2019-10-03 Basic functionality working. Interfacing to Blynk functional. Calibration is WIP.
2019-10-04 Blynk value sending functional. Calibration still WIP.
2019-10-04 Basic battery monitoring added.
2019-10-04 Basic calibration working
2019-10-09 Better calibration added. Properf FIFO handling a WIP
2019-10-12 Added vertical calibration
2019-10-12 Added motor control scripts
2019-10-13 Slowed battery checking, more robust IMU failure handling
2019-10-15 Added hardware designs
    [Arm Base 3.stl, Arm Lid 3.stl, Charger Base 3.stl, Charger Lid 3.stl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]
2019-10-15 Added wrist form apparatus design
    [Arm 2.stl, Hand 2.stl]
2019-10-15 Added wiring_flow.jpg
2019-10-15 Added images
    [alog3.csv, log.csv, qlog.csv, qlog2.csv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]
2019-10-16 Moving things around
    [Arm 2.stl, Arm Base 3.stl, Arm Lid 3.stl, Charger Base 3.stl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]
2019-10-17 Added circuit images
